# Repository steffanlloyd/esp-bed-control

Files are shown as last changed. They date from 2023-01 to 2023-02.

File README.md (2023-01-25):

# esp-bed-control

This project defines a voice-control module designed to allow voice control of hospital beds for. This allows patients who are unable to use the pendant normally attached to the bed to adjust their bed position themselves.

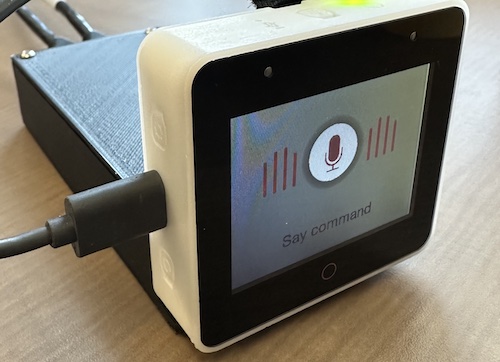
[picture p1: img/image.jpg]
Image of ESP Bed Control Box


The device is based on the ESP BOX by espressif. This is a self-contained unit that includes an ESP32-S3, speakers, a microphone, and a screen. It also includes software for voice control.

The device itself is designed to be modular for use on a wide variety of beds. It consists of 3 major components:
  - The ESP Box (performs the voice recognition, user feedback, and logic).
  - The ESP hospital bed dock. This is a custom PCB that the ESP box can dock onto. It takes signals from 6 GPIO pins and routes them to 6 solid-state relays. These relays act as "loop closures", simulating a real hospital bed pendant. These 6 loop closures have 12 associated leads that are mapped to the first 12 pins of a male DB25 port. The dock also has a USB-C port for charging, and an RJ45 port that was only included to allow for future expansion of the project, but is not currently in use.
  - The hospital bed interface PCB. This is another custom PCB which must be designed specifically for the bed in question. Its role is to take the loop closers from the DB25 port on the dock PCB, and map them to the right pins of the pendant. It should connect to the bed, and to the pendant, such that the pendant continues to work as normal. We have designed one such interface board for the "New Span America" hospital beds. 

The hookup diagram is shown below.

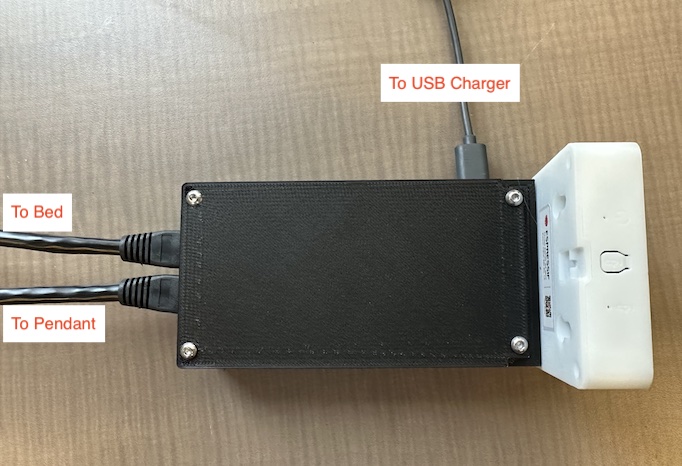
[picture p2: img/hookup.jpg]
Image of ESP Bed Control Hookup


The entire device is housed inside a 3D printed shell. The STL files for this shell are included in the /cad folder.

Documentation can be found in ``docs/instructions.pdf``.

## Available Commands

When you plug in the ESP box (after its been flashed and assembled), it will startup for a short period then "ding" to indicate that it is ready. It can then be woken with the wake word "Hi E.S.P.". Once it has woken, any of the following commands may be issued:
- Headrest up/down
- Legrest up/down
- Bed up/down
Each of these commands can be modified with "a little bit", "way", or "fully", e.g. "Headrest a little up", "Headrest way up", or "Headrest fully up". The nominal command closes the relay for 2 seconds. "A little bit" is only 1 second, "way" is 4 seconds, and "fully" is 15 seconds.

## PCB Manufacturing

To manufacture the PCB, you will need to have some experience with custom PCB manufacturing. Kicad schematics and PCB layouts are provided for all boards, as well as PDF's. These are all in the /pcb folder.

## Programming the ESP Box

Programming the ESP box is a bit challenging, since documentation is limited. However, our program is relatively well commented and is included here under the /src folder. The main components of this software are listed below:
  - ``main.c``: Initiates the program, assigns the GPIO pins
  - ``/gui/ui_sr.c``: Includes the code to how the UI displays for the speech recognition.
  - ``/gui/ui_main.c``: Includes other code on how the UI works
  - ``/app/app_audio.c``: Initializes the speaker output.
  - ``/app/app_lvgl.c``: Initializes the screen of the devices.
  - ``/app/app_sr_handler.c``: Contains the logic of how to respond to different voice commands.
  - ``/app/app_sr.c``: Contains code for the actual voice recognition itself.

## Flashing the ESP Box

To flash the ESP box, follow these steps.
1. Open/Install VScode, and install the Espressif IDE plugin. [Instructions here](https://docs.espressif.com/projects/esp-idf/en/latest/esp32/get-started/index.html). You may take some time to get familiar with the programming environment.
2. Next, setting up development environment. Please refer to [ESP-IDF (release/v5.0)](https://docs.espressif.com/projects/esp-idf/en/release-v4.4/esp32s3/get-started/index.html#installation-step-by-step) Installation Step by Step.
3. Run command ``git clone --recursive https://github.com/espressif/esp-box.git`` somewhere on your machine to download the code of this project and then switch the ESP-IDF version to specified version.
4. Open up the ``/src`` folder and link the "components" of the project in ``CMakeLists.txt``. E.g., replace the lines
  ```
  set(EXTRA_COMPONENT_DIRS
      path/to/esp-box/components
      )
  ```
5. Connect, build and flash the device.

## Customizing the voice commands

In VS code, open the ESP-IDF Terminal (it may already be open, otherwise there is a button in the bottom that opens it). To customize the voice commands you need to run the ``idf.py menuconfig`` command, and customize the commands that the board listens to.  This is done under the ``ESP Speech Recognition`` menu item, followed by ``Add English speech commands``. You may also customize the wakeword under the ``Select wake words`` menu item.

You will need to generate the G2P phrase for each voice command. A description of how to do this is given in ``esp-box/components/esp-sr/tool``. A list of the G2P commands for all the default commands are given in ``docs/commands.xlsx``.

Once this is complete, you should modify the handling of each of these voice commands with appropriate modifications to ``app/app_sr_handler.c``. Each voice command in the menuconfig settings is keyed to its ID number, so the ``app_sr_handler`` code simply runs that ID through a switch statement to run the appropriate code.

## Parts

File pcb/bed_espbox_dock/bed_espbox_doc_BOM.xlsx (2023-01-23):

BOM
Name | Qty | ID | Digikey Part ID | Component ID
SS Relay | 6 | CPC1017NTR | CLA233CT-ND | U1,U2,U3,U4,U5,U6
RJ45 Jack | 1 | 54602-908LF | 609-1046-ND | J4
USB C | 1 | USB4085-GF-A | 2073-USB4105-GF-ACT-ND | J6
DB25 Male | 1 | A-DS 25 A/KG-T2S | AE10980-ND | J5
Resistor array | 2 | CAY16-561J4LF | CAY16-561J4LFCT-ND | RN1,RN2
Grounding resistor | 2 | ERJ-2GEJ512X | P5.1KJCT-ND | R1,R2
Male header 12 | 2 | PH2-12-UA | 2057-PH2-12-UA-ND | J1,J2
Male header 4 | 1 | PH2-04-UA | 2057-PH2-04-UA-ND | J3

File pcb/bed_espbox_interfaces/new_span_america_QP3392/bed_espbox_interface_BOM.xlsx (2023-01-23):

BOM
Name | Qty | ID | Digikey Part ID | Component ID
DB25 Female | 1 | A-DF 25 A/KG-T4S | AE10937-ND | J1
RJ50 Jack | 2 | 54602-910LF | 609-1047-ND | J2,J3
Diode 2x | 2 | MMBD4448HTM-7-F | MMBD4448HTM-FDICT-ND | D1,D2

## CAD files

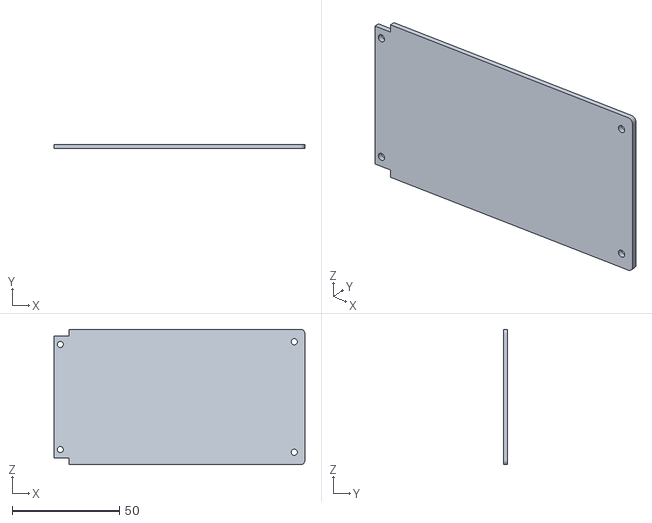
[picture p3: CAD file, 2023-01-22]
cad/esp-box-shell-upper.stl
117.0 x 2.00 x 63.0

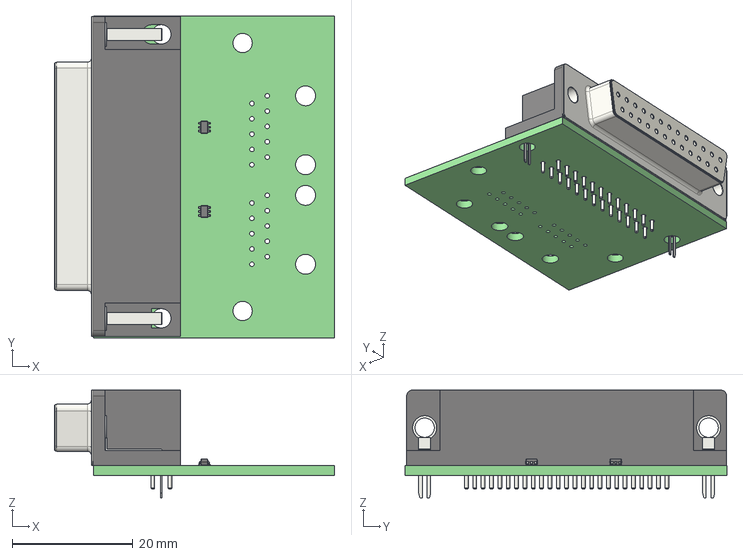
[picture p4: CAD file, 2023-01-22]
pcb/bed_espbox_interfaces/new_span_america_QP3392/bed_espbox_interface.step
46.4 x 53.3 x 17.9 mm
bed_espbox_interface PCB

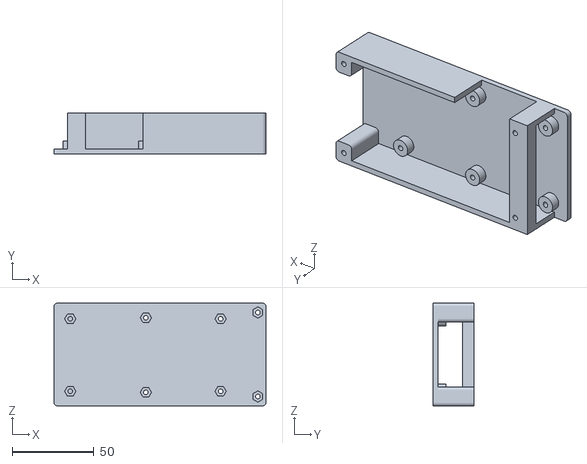
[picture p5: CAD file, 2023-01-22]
cad/esp-box-shell-lower.stl
130.0 x 25.0 x 63.0

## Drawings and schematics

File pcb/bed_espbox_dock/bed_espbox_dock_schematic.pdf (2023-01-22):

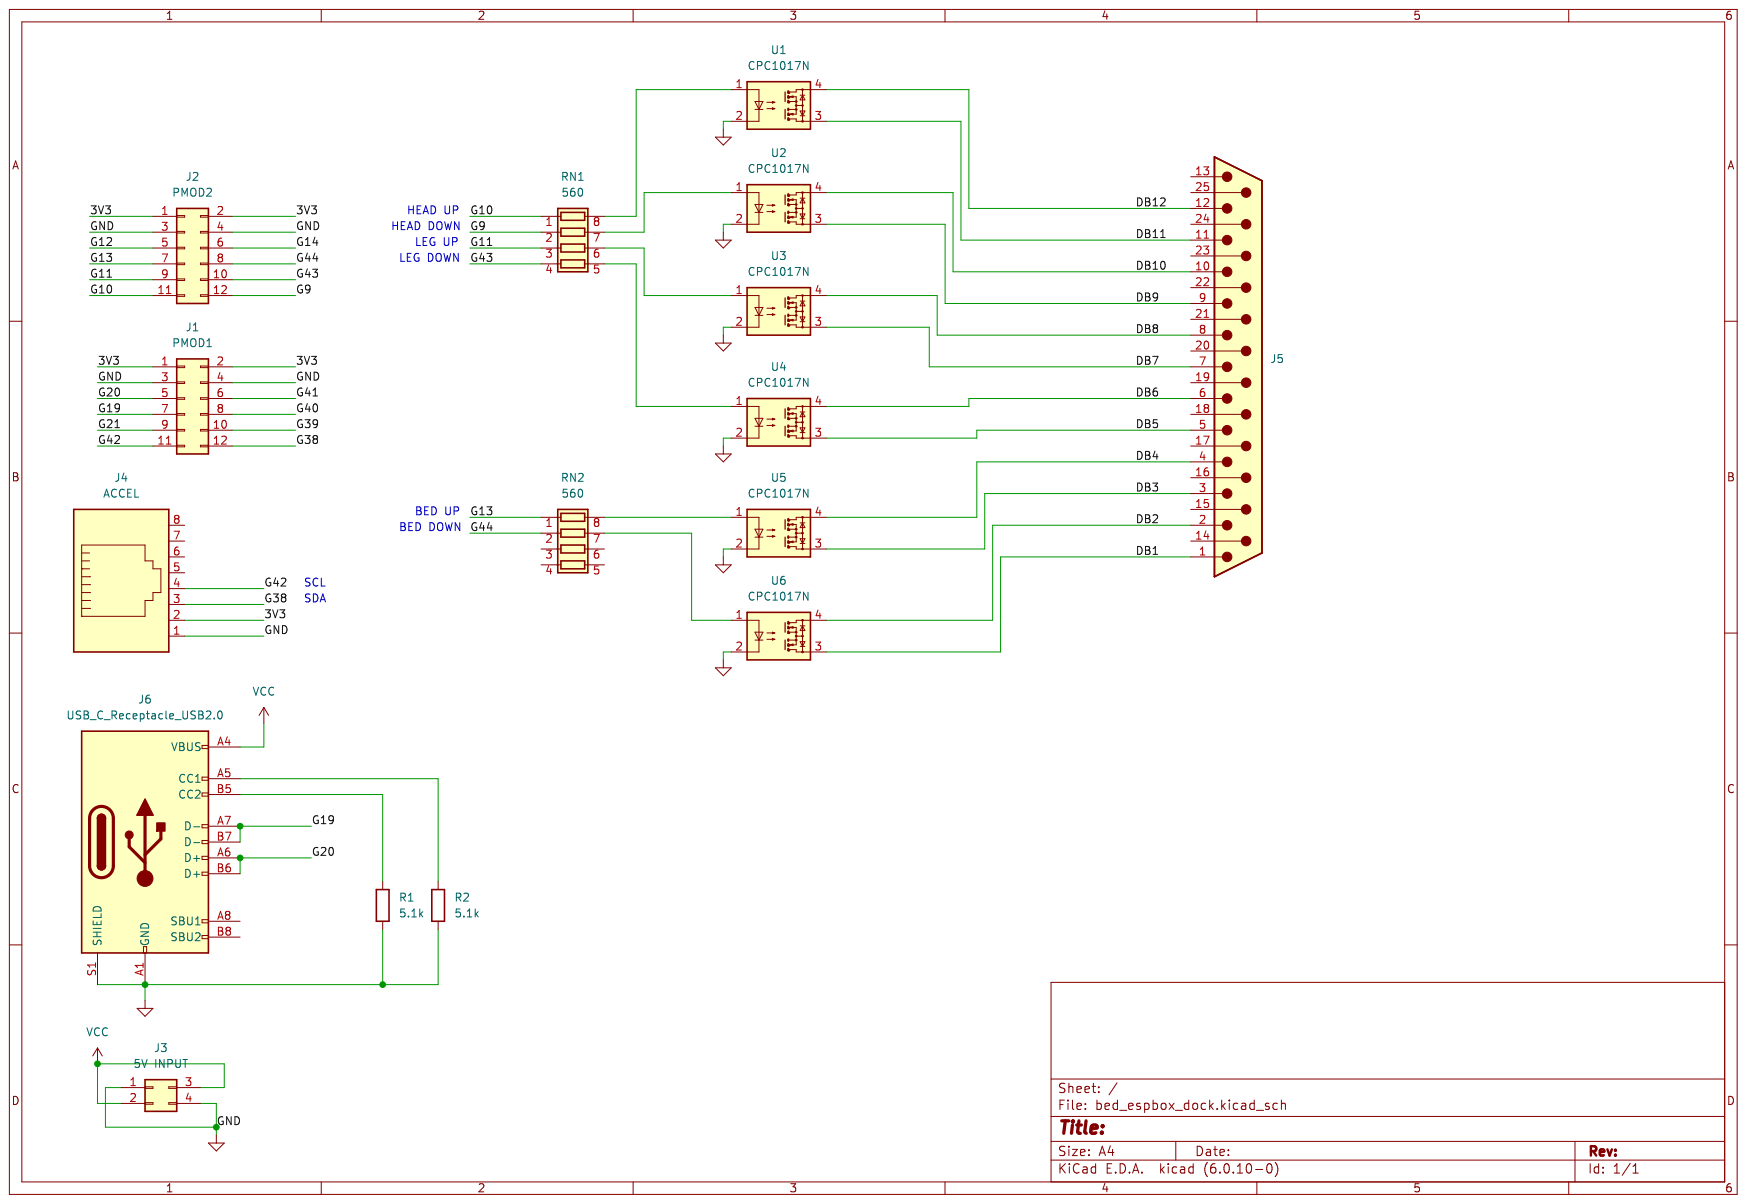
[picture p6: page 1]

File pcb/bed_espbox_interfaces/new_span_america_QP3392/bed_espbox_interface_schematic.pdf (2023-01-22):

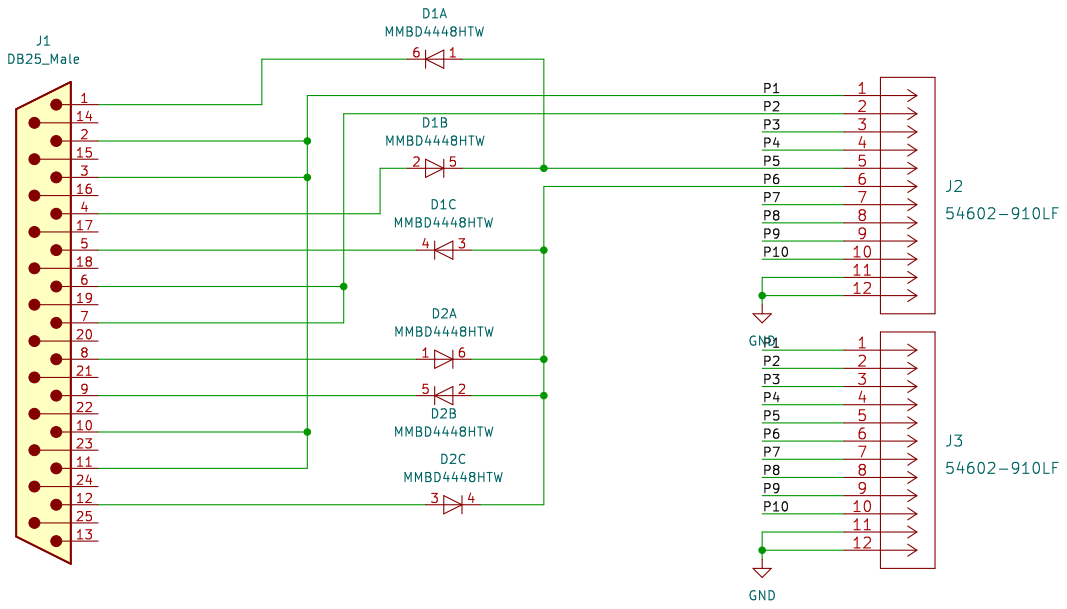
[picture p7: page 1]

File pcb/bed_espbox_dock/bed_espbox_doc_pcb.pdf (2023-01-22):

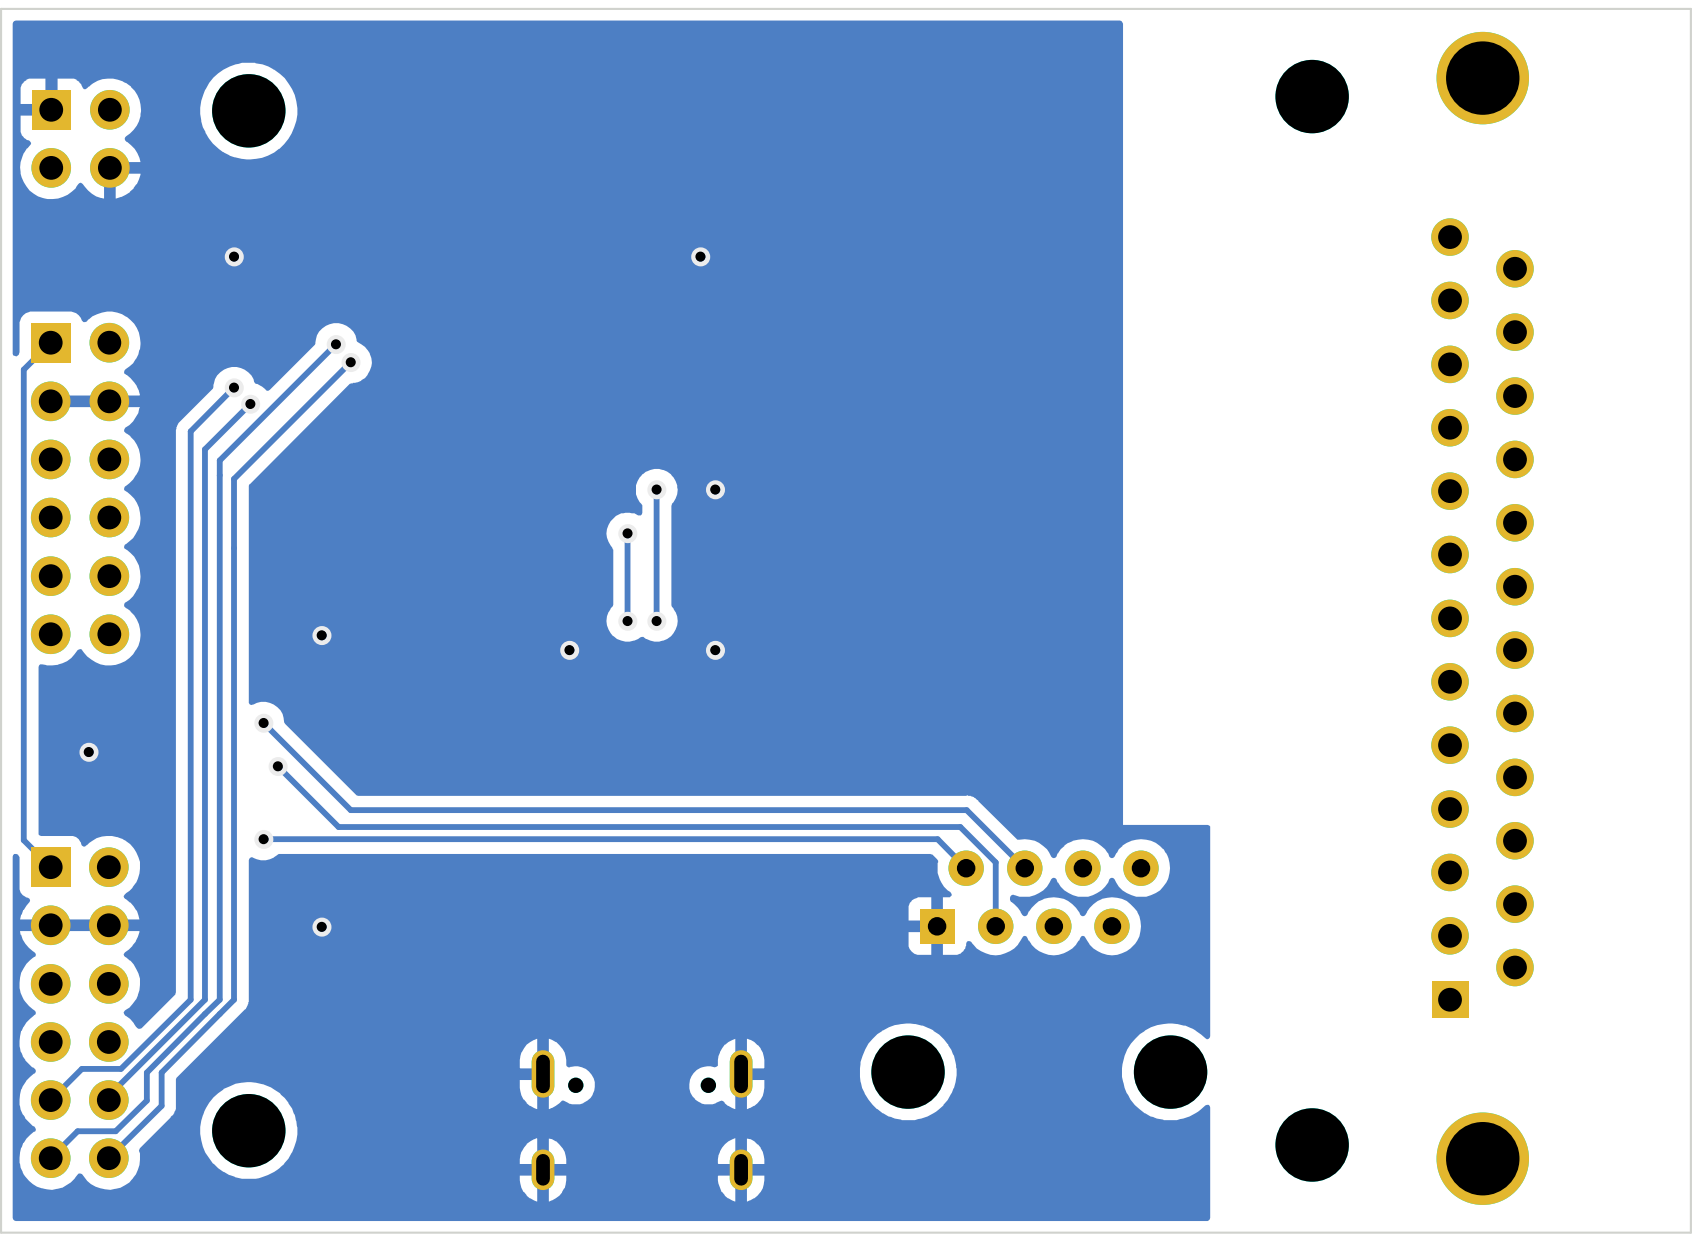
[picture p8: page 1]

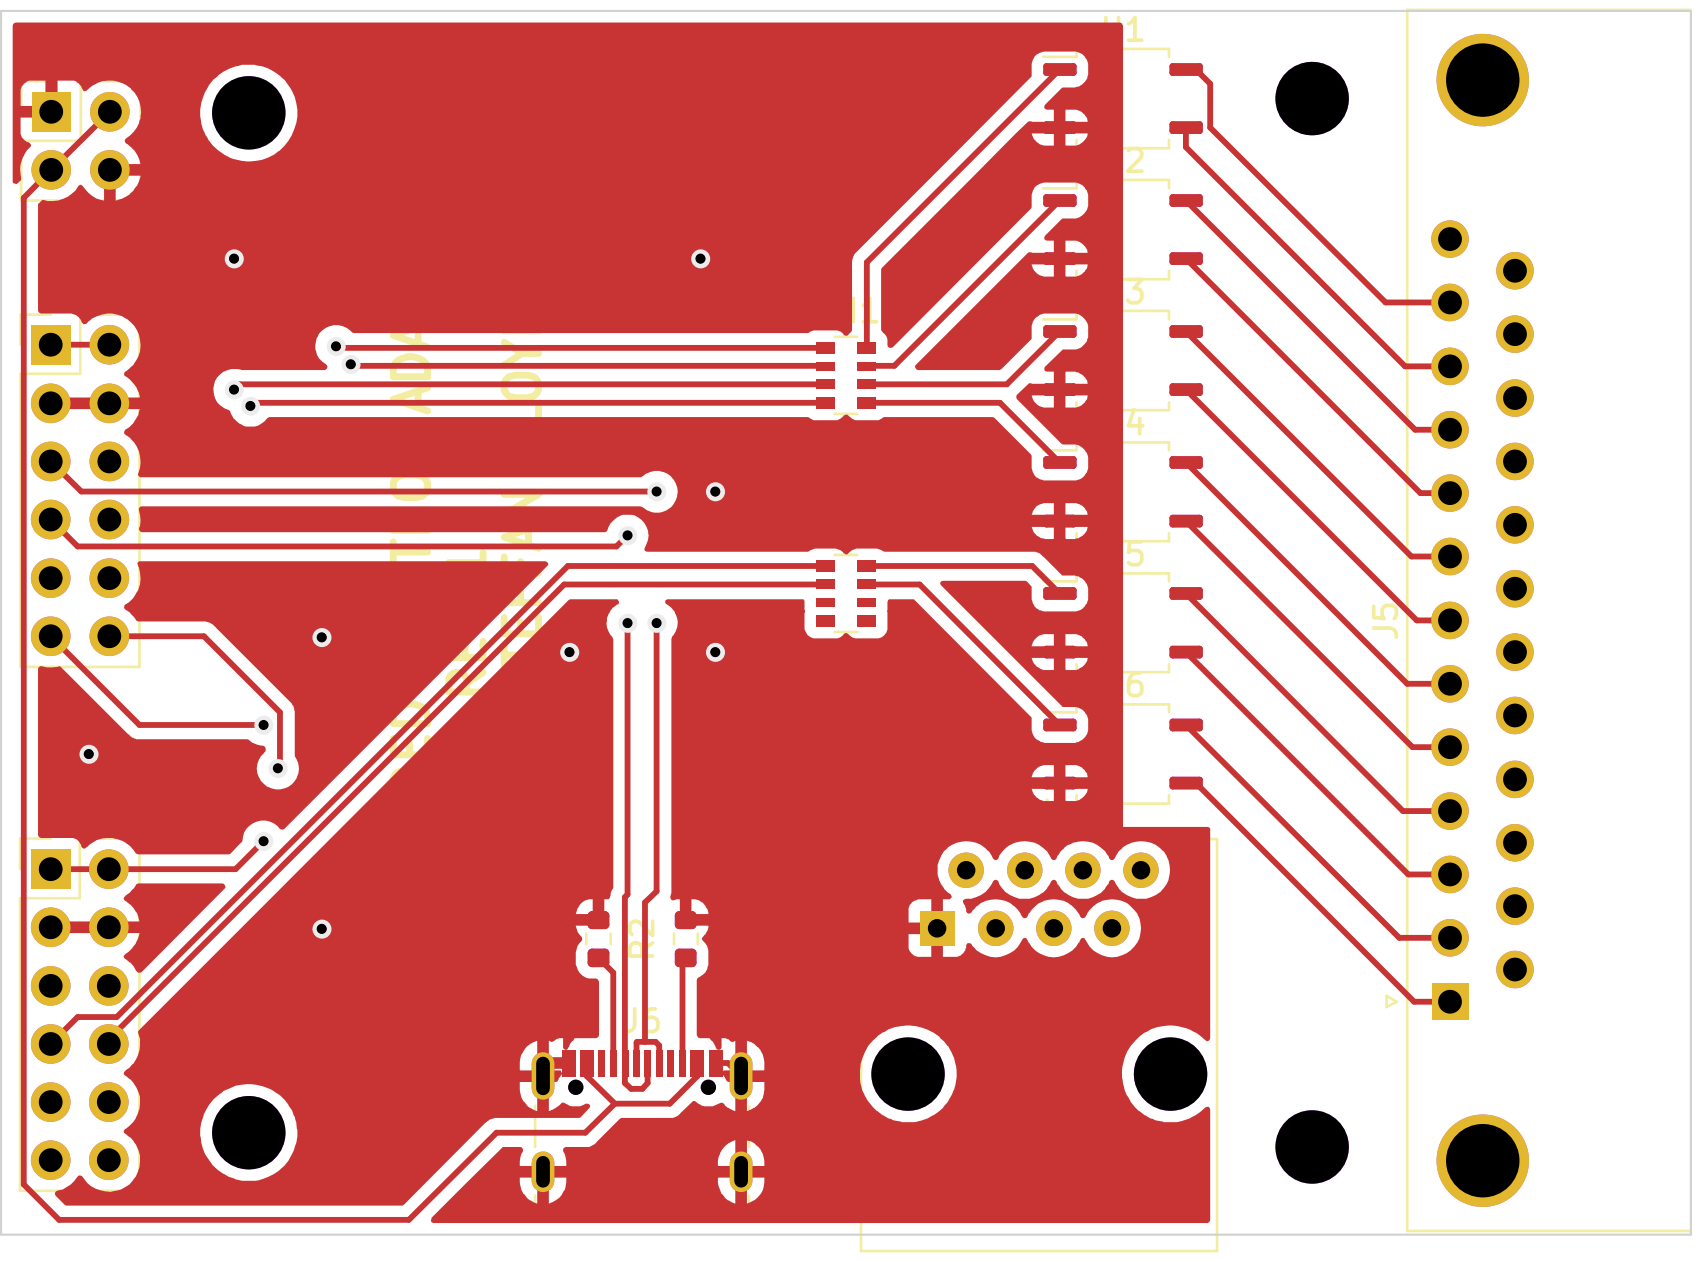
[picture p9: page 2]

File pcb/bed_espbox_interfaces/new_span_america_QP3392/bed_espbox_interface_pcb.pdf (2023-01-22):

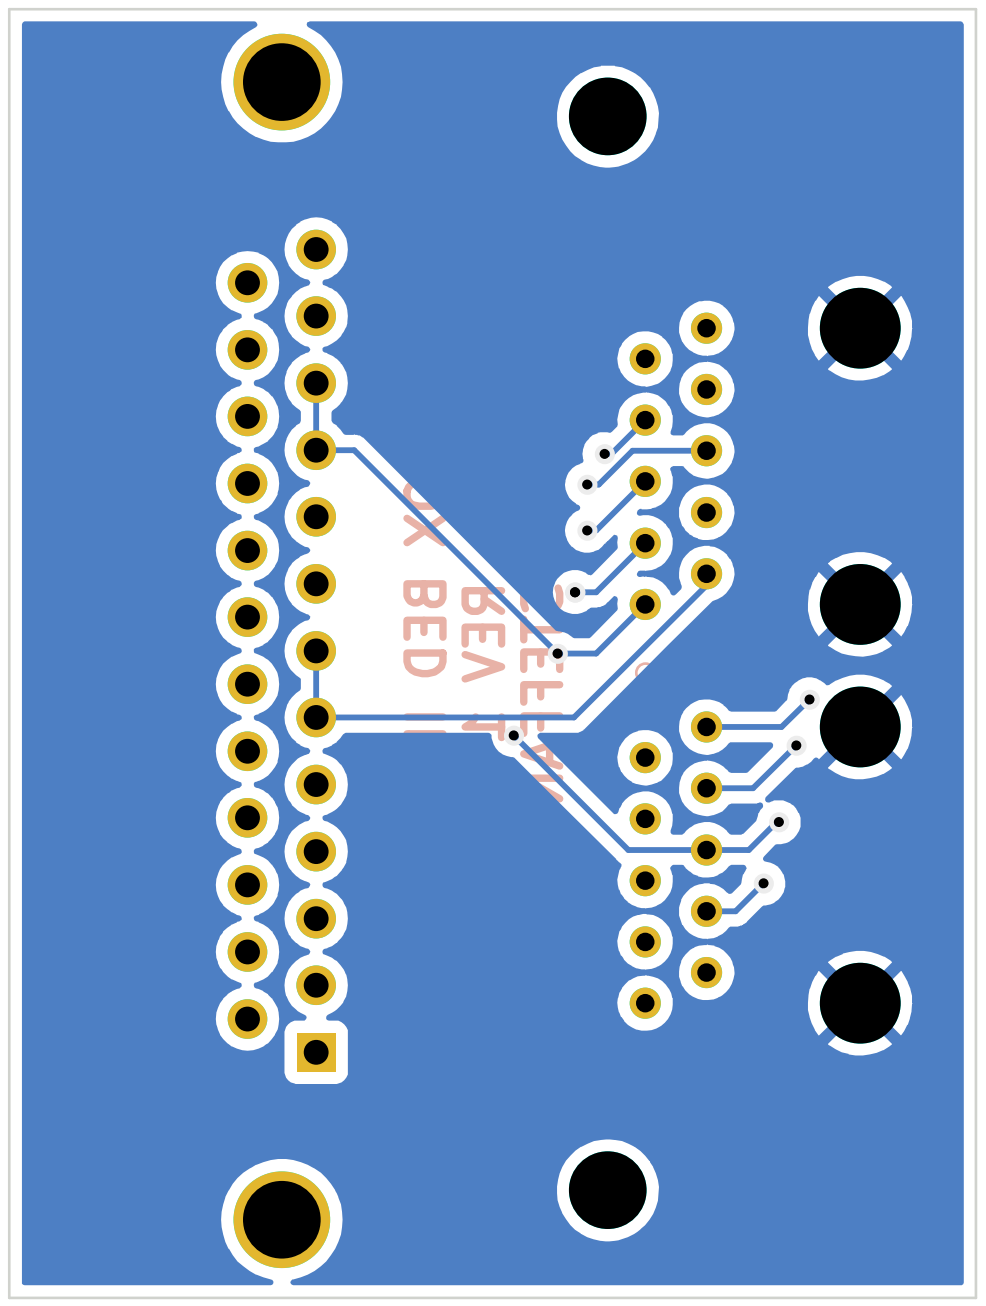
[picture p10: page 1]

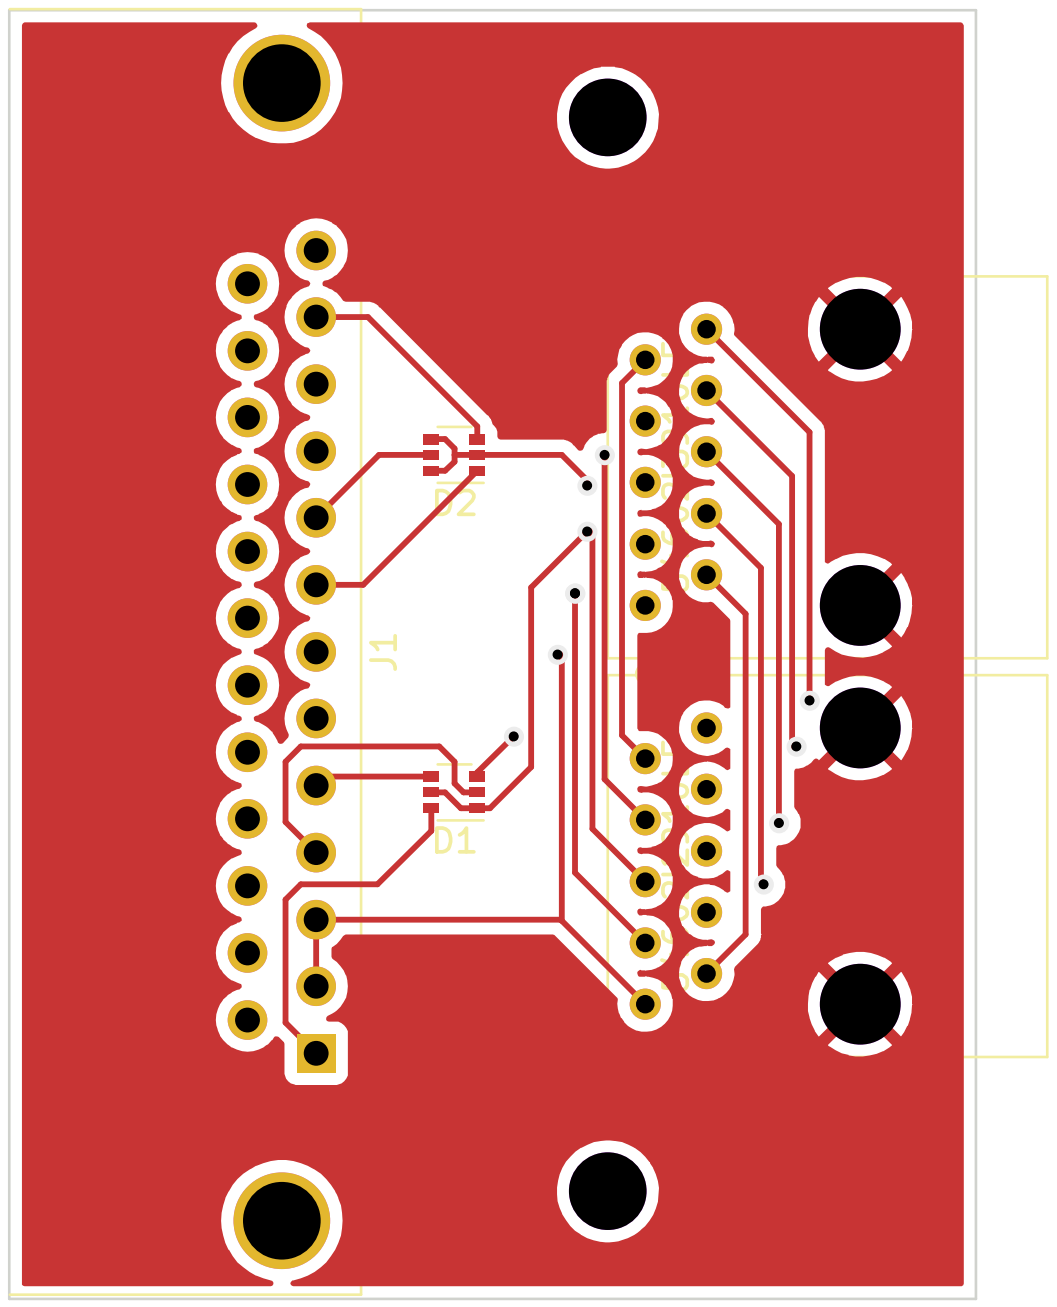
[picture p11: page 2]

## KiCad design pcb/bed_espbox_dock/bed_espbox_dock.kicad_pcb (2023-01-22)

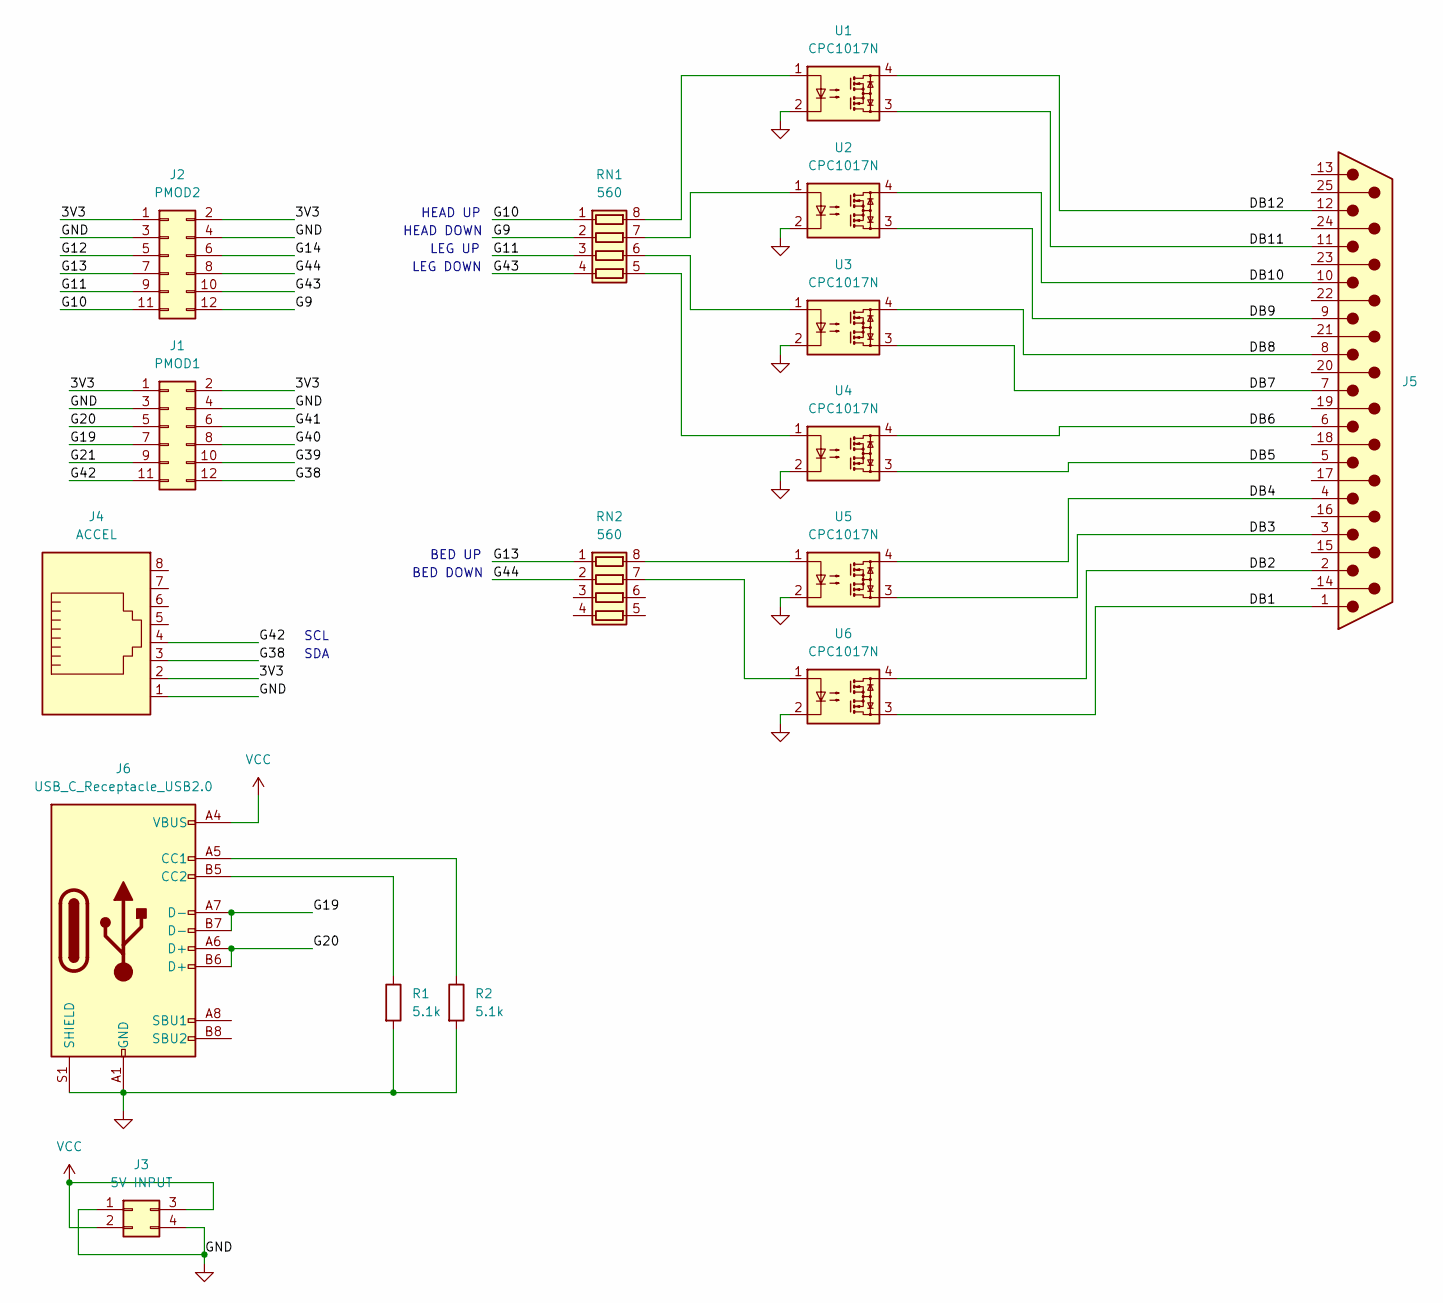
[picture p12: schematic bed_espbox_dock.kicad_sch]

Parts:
J1: PMOD1; PinHeader_2x06_P2.54mm_Vertical
J2: PMOD2; PinHeader_2x06_P2.54mm_Vertical
J3: 5V INPUT; PinHeader_2x02_P2.54mm_Vertical
J4: ACCEL; RJ45_Amphenol_54602-x08_Horizontal
J5: DB25_Male; DSUB-25_Male_Horizontal_P2.77x2.84mm_EdgePinOffset7.70mm_Ho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
J6: USB_C_Receptacle_USB2.0; USB_C_Receptacle_GCT_USB4105-xx-A_16P_TopMnt_Horizontal
R1, R2: 5.1k; R_0603_1608Metric
RN1, RN2: 560; R_Array_Convex_4x0603
U1, U2, U3, U4, U5, U6: CPC1017N; SOP-4_3.8x4.1mm_P2.54mm

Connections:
/3V3: J1.1, J1.2, J2.1, J2.2, J4.2
/DB1: J5.1, U6.3
/DB2: J5.2, U6.4
/DB3: J5.3, U5.3
/DB4: J5.4, U5.4
/DB5: J5.5, U4.3
/DB6: J5.6, U4.4
/DB7: J5.7, U3.3
/DB8: J5.8, U3.4
/DB9: J5.9, U2.3
/DB10: J5.10, U2.4
/DB11: J5.11, U1.3
/DB12: J5.12, U1.4
/G9: J2.12, RN1.2 (R2.1)
/G10: J2.11, RN1.1 (R1.1)
/G11: J2.9, RN1.3 (R3.1)
/G12: J2.5
/G13: J2.7, RN2.1 (R1.1)
/G14: J2.6
/G19: J1.7, J6.A7 (D-), J6.B7 (D-)
/G20: J1.5, J6.A6 (D+), J6.B6 (D+)
/G21: J1.9
/G38: J1.12, J4.3
/G39: J1.10
/G40: J1.8
/G41: J1.6
/G42: J1.11, J4.4
/G43: J2.10, RN1.4 (R4.1)
/G44: J2.8, RN2.2 (R2.1)
GND: J1.3, J1.4, J2.3, J2.4, J3.1, J3.4, J4.1, J6.A1 (GND), J6.A12 (GND), J6.B1 (GND), J6.B12 (GND), J6.S1 (SHIELD), R1.2, R2.2, U1.2, U2.2, U3.2, U4.2, U5.2, U6.2
unnamed: J6.A5 (CC1), R2.1
unnamed: J6.B5 (CC2), R1.1
unnamed: RN1.5 (R4.2), U4.1
unnamed: RN1.6 (R3.2), U3.1
unnamed: RN1.7 (R2.2), U2.1
unnamed: RN1.8 (R1.2), U1.1
unnamed: RN2.7 (R2.2), U6.1
unnamed: RN2.8 (R1.2), U5.1
VCC: J3.2, J3.3, J6.A4 (VBUS), J6.A9 (VBUS), J6.B4 (VBUS), J6.B9 (VBUS)

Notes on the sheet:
BED DOWN
SCL
SDA
LEG DOWN
BED UP
LEG UP
HEAD DOWN
HEAD UP

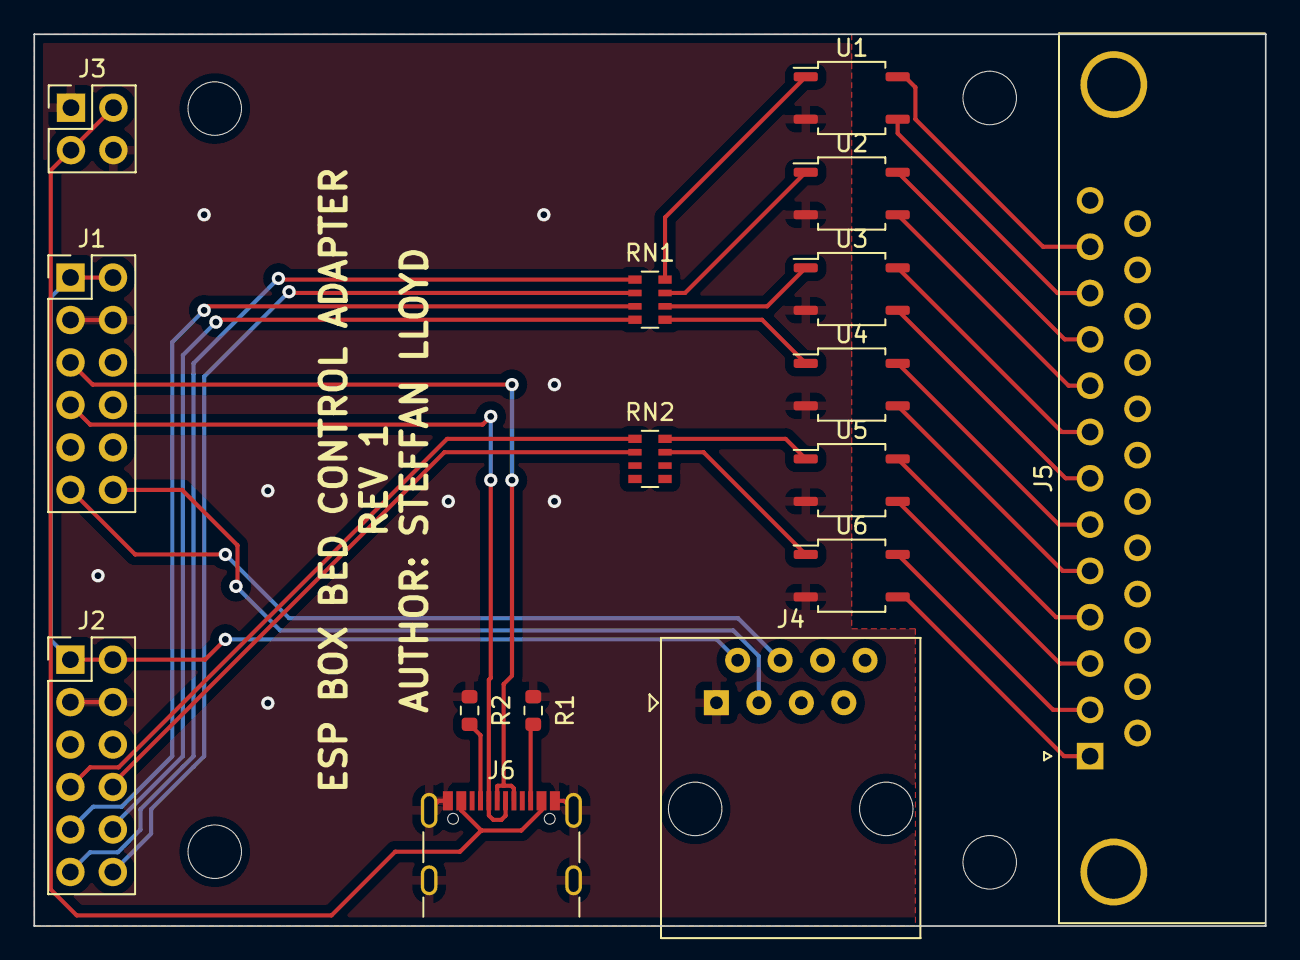
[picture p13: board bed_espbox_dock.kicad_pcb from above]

Board: 2 copper layers, 73.7 x 53.3 mm, 16 parts (0 on the bottom side), 33 nets.

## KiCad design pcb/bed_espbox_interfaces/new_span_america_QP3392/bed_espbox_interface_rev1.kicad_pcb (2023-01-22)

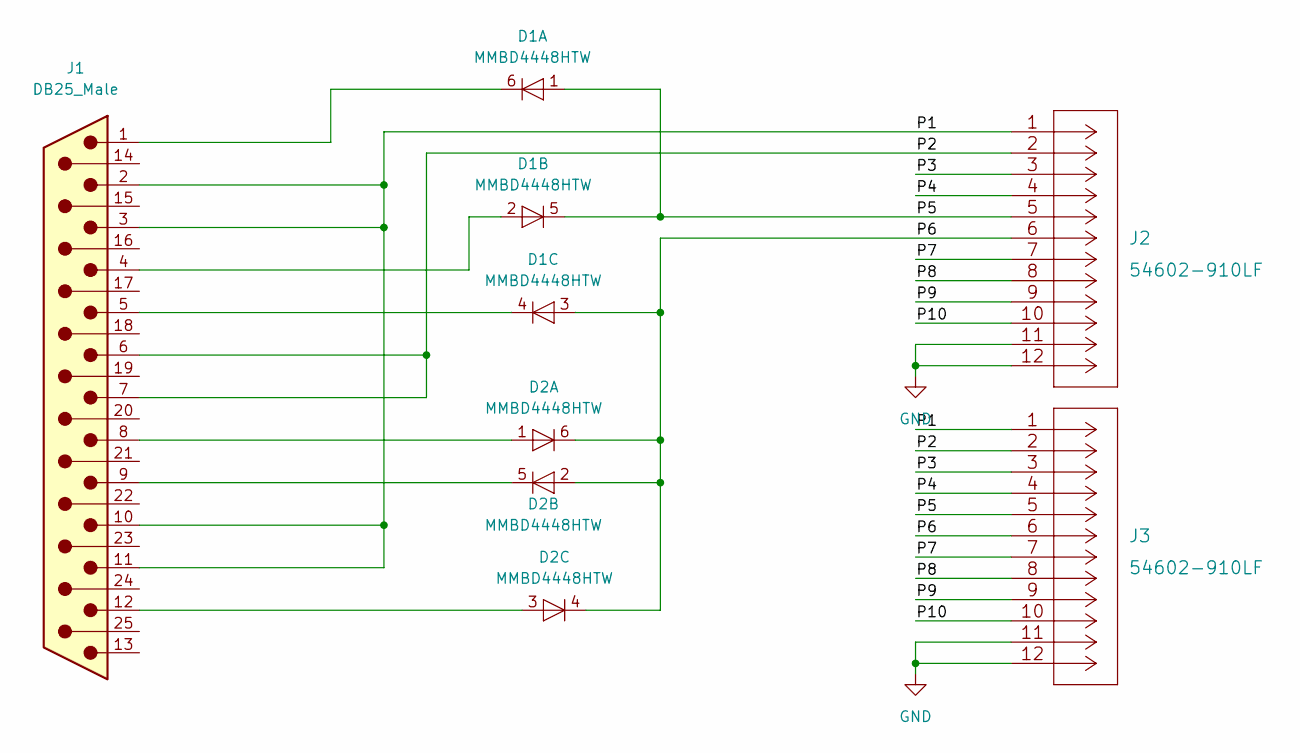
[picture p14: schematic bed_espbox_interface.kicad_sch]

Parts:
D1, D2: MMBD4448HTW; SOT-363_SC-70-6
J1: DB25_Male; DSUB-25_Female_Horizontal_P2.77x2.84mm_EdgePinOffset9.90mm_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
J2, J3: 54602-910LF

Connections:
/P1: J1.2, J1.3, J1.10, J1.11, J2.1, J3.1
/P2: J1.6, J1.7, J2.2, J3.2
/P3: J2.3, J3.3
/P4: J2.4, J3.4
/P5: D1.1 (A), D1.5 (K), J2.5, J3.5
/P6: D1.3 (A), D2.2 (A), D2.4 (K), D2.6 (K), J2.6, J3.6
/P7: J2.7, J3.7
/P8: J2.8, J3.8
/P9: J2.9, J3.9
/P10: J2.10, J3.10
GND: J2.11, J2.12, J3.11, J3.12
unnamed: D1.6 (K), J1.1
unnamed: D1.2 (A), J1.4
unnamed: D1.4 (K), J1.5
unnamed: D2.1 (A), J1.8
unnamed: D2.5 (K), J1.9
unnamed: D2.3 (A), J1.12

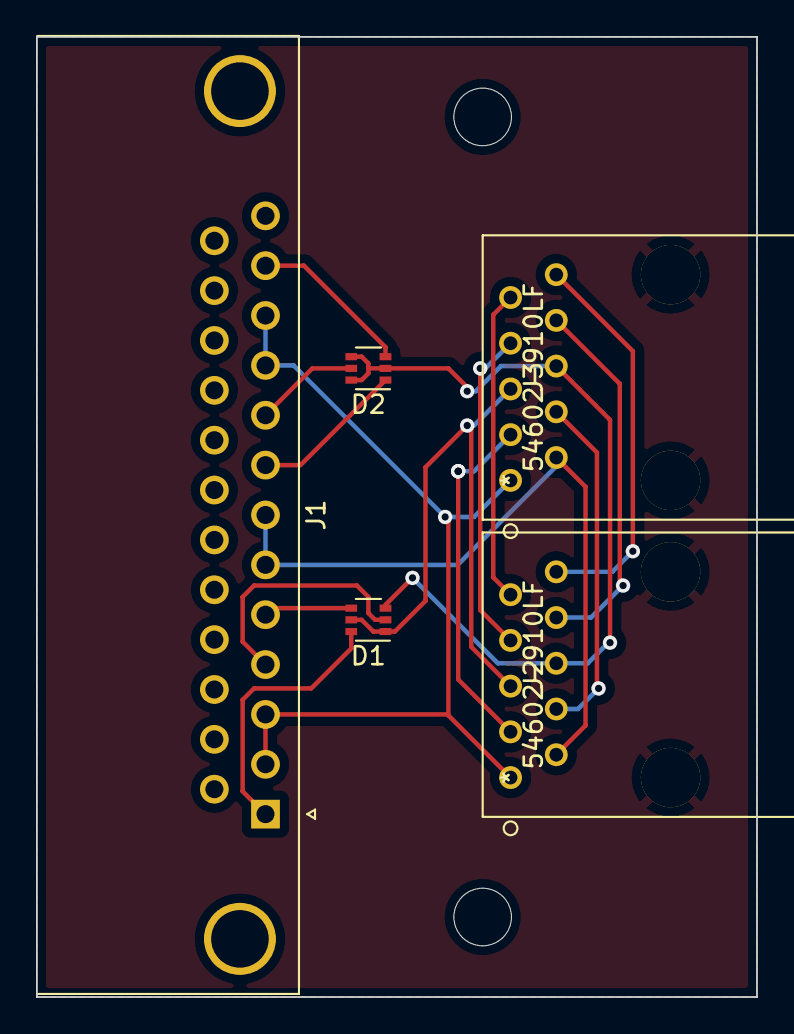
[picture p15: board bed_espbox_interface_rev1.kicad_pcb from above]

Board: 2 copper layers, 40.0 x 53.3 mm, 5 parts (0 on the bottom side), 17 nets.

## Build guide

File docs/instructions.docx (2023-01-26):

ESP Hospital Bed Controller: Instructions

This system allows a hospital bed to be controlled via voice commands. This system is tested with the New Span America Hospital Bed, Pendant QP3392.

Usage:

Each command must be preceded by the wake word. The wake word is “Hi. E.S.P.” Then, any of the following commands may be issued:

Normal commands:

“Headrest up” or “Headrest down” | Presses the headrest up/down button for 2 seconds.
“Legrest up” or “Legrest down” | Presses the legrest up/down button for 2 seconds.
“Bed up” or “Bed down” | Presses the bed up/down button for 2 seconds.

Modified commands

“Headrest a little up” or “Headrest a little down” | Presses the headrest up/down button for 1 seconds.
“Legrest a little up” or “Legrest a little down” | Presses the legrest up/down button for 1 seconds.
“Bed a little up” or “Bed a little down” | Presses the bed up/down button for 1 seconds.
“Headrest way up” or “Headrest way down” | Presses the headrest up/down button for 4 seconds.
“Legrest way up” or “Legrest way down” | Presses the legrest up/down button for 4 seconds.
“Bed way up” or “Bed way down” | Presses the bed up/down button for 4 seconds.
“Headrest fully up” or “Headrest fully down” | Presses the headrest up/down button for 15 seconds.
“Legrest fully up” or “Legrest fully down” | Presses the legrest up/down button for 15 seconds.
“Bed fully up” or “Bed fully down” | Presses the bed up/down button for 15 seconds.

Setup

Setup the device as per the diagram below. The remote should be plugged in to one of the RJ50 ports at the base of the device. Then, the second RJ50 port should be connected with an RJ50 cable to the socket where the pendant normally connects to the bed. Finally, a USB-C cable should be plugged into the USB socket on the side of the device, and the other side connected to a USB charger.


Note: If the usb socket on the black body doesn’t work, you may use the USB-C port on the other side of the white box instead.

Troubleshooting

In case of issues, please try the following steps:

1. Restart the device. This can be done by cycling power to the ESB box. Simply unplug the USB cable on the side of the device, then plug it back in again.
2. If this does not correct the issue, email Steffan Lloyd (steffan.lloyd@icloud.com) and Nick Berezny (Nicholas.Berezny@carleton.ca) to describe the issue.
3. If the functioning of the bed is affected (e.g. if the pendant no longer works), the bed should resume normal functioning by disconnecting the ESB box entirely. Unplug the pendant from the ESP box, then plug it directly into the bed.

BED COMMANDS

Wake word: “Hi E.S.P.”

HEADREST UP | HEADREST DOWN
LEGREST UP | LEGREST DOWN
BED UP | BED DOWN

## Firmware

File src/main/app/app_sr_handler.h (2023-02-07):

/*
 * SPDX-FileCopyrightText: 2021 Espressif Systems (Shanghai) CO LTD
 *
 * SPDX-License-Identifier: CC0-1.0
 */

#pragma once

#include <stdbool.h>
#include "esp_err.h"

#define LED_RED 39
#define LED_GREEN 40
#define LED_BLUE 41
#define GPIO_HEAD_DOWN 10
#define GPIO_HEAD_UP 9
#define GPIO_LEG_DOWN 11
#define GPIO_LEG_UP 43
#define GPIO_BED_DOWN 13
#define GPIO_BED_UP 44

void sr_handler_task(void *pvParam);

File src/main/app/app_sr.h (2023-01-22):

/*
 * SPDX-FileCopyrightText: 2015-2022 Espressif Systems (Shanghai) CO LTD
 *
 * SPDX-License-Identifier: Unlicense OR CC0-1.0
 */

#pragma once

#include <stdbool.h>
#include "esp_err.h"
#include "esp_afe_sr_models.h"
#include "esp_mn_models.h"

#define SR_CONTINUE_DET 1

/**
 * @brief Speech command string
 *
 */
#define STR_DELIMITER       ";"

#define STR_TIMEOUT         "Timeout"
#define STR_WAKEWORD        "Hi ESP"
#define STR_LIGHT_RED       "Turn Red"
#define STR_LIGHT_GREEN     "Turn Green"
#define STR_LIGHT_BLUE      "Turn Blue"
#define STR_LIGHT_WHITE     "Turn White"
#define STR_LIGHT_ON        "Turn On The Light"
#define STR_LIGHT_OFF       "Turn Off The Light"
#define STR_LIGHT_COLOR     "Customize Color"

#define VOICE_LIGHT_RED     CONFIG_EN_SPEECH_COMMAND_ID0
#define VOICE_LIGHT_GREEN   CONFIG_EN_SPEECH_COMMAND_ID1
#define VOICE_LIGHT_BLUE    CONFIG_EN_SPEECH_COMMAND_ID2
#define VOICE_LIGHT_WHITE   CONFIG_EN_SPEECH_COMMAND_ID3
#define VOICE_LIGHT_ON      CONFIG_EN_SPEECH_COMMAND_ID4
#define VOICE_LIGHT_OFF     CONFIG_EN_SPEECH_COMMAND_ID5
#define VOICE_LIGHT_COLOR   CONFIG_EN_SPEECH_COMMAND_ID6

typedef struct {
    wakenet_state_t wakenet_mode;
    esp_mn_state_t state;
    int command_id;
} sr_result_t;

/**
 * @brief User defined command list
 *
 */
typedef enum {
    SR_CMD_SET_RED = 0,
    SR_CMD_SET_GREEN,
    SR_CMD_SET_BLUE,
    SR_CMD_SET_WHITE,
    SR_CMD_LIGHT_ON,
    SR_CMD_LIGHT_OFF,
    SR_CMD_CUSTOM_COLOR,
} sr_cmd_t;

/**
 * @brief Start speech recognition task
 *
 * @return
 *    - ESP_OK: Success
 *    - ESP_ERR_NO_MEM: No enough memory for speech recognition
 *    - Others: Fail
 */
esp_err_t app_sr_start();

/**
 * @brief Reset command list
 *
 * @param command_list New command string
 * @return
 *    - ESP_OK: Success
 *    - ESP_ERR_NO_MEM: No enough memory for err_id string
 *    - Others: Fail
 */
esp_err_t app_sr_reset_command_list(char *command_list);

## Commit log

2023-01-22 Added codebase and docs
    [commands.xlsx, partitions.csv]
2023-01-22 Added cad and electrical files
    [BOM.xlsx, bed_espbox_dock.kicad_pcb, bed_espbox_dock.kicad_sch, bed_espbox_interface.kicad_sch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]
2023-01-23 Updated readme and reorganized
    [BOM.xlsx, bed_espbox_doc_BOM.xlsx, bed_espbox_interface.kicad_sch, bed_espbox_interface.step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]

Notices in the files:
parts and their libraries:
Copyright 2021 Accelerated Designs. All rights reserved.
